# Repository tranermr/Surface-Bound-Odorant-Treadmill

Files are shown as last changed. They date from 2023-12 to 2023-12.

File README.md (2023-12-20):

# Surface-Bound-Odorant-Treadmill

One of the important subsets of odors sources used in olfactory navigation is surface-bound sources, which can broadly take the form of point sources or trails. Here, we present an automated treadmill design capable of dynamically printing odor trails of arbitrary lengths and configurations, and with closed-loop control of speed based on the animal’s movement. This design is presented and the utility demonstrated in a corresponding paper studying surface-bound odor trail interactions in locusts (in submission).The uploaded design incorporates some improvements not reflected in the version used in the published paper (i.e. the modification of some components to reduce paper jams, and quality of life improvements). The design is provided in four directories, containing the mechanical components, the electrical component design, and the software and firmware for operation.

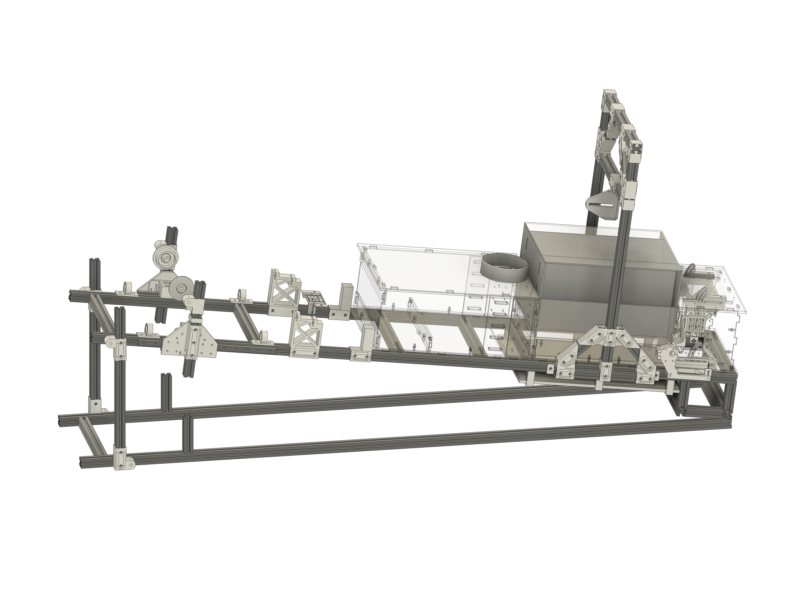
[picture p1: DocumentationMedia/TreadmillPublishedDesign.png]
Photo of assembled treadmill


The treadmill is designed to enable long-duration interactions with surface-bound odor trails of arbitrary length. Below you can see a video of a locust engaged in a bout of trail following with an odor trail, where the treadmill advances once the locust approaches the front of the behavior chamber, revealing more trail for the locust to interact wtih.

Video of locust following an odor trail

The treadmill is comprised of a series of modules sequentially connected and mounted on an 80-20 frame enabling different slopes to be configured. The design of the mechanical components is provided as an .f3d file, openable using Fusion 360, which is available in [educational](https://www.autodesk.com/campaigns/education/fusion-360-education), or [professional or free versions](https://www.autodesk.com/products/fusion-360/personal/compare).

In the mechanical design file, the design is organized by modules, with the exception of the 'behavior chamber' and 'driver' modules, which are merged in the present design. The organizational structure is arranged to reflect all modules independently for any future revisions. Further details regarding each of the design categories is provided below.

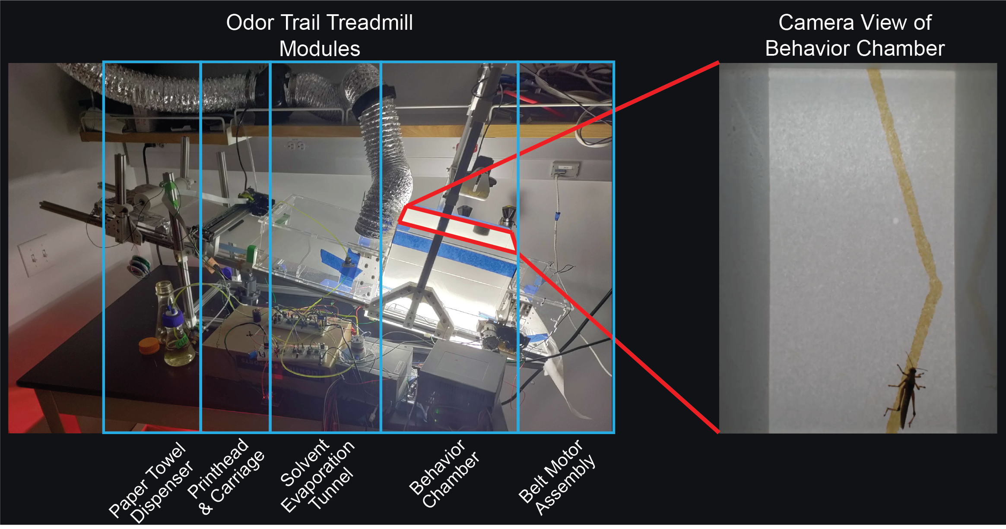
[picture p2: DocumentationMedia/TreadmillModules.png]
Treadmill modules, and top view of behavior chamber


## Mechanical Components
The components of each treadmill module are broken out below. Each module section contains a list of the parts not 3D printed or laser cut from acrylic, as well as suggestions to ease assembly.

### Frame
The treadmill frame is made of 20mm extruded aluminum (2020). The recommended parts list for the frame is

<ins>Misumi</ins>
| Description				| Part Number 		| Quantity|
| ------------- 			|:-------------:	| -----:|
| Aluminum Extrusions 			| HFS5-2020-1500 	| 6 	|
| Aluminum 20mm Brace - optional	| HBLFSNF5-C-SEC 	|   8 	|
| Square Nuts (100 Pack)		| HNKK5-5      		|   2 	|
| Hinges 				| HHPSN5-SET      	|   2 	|

<ins>Grainger</ins>
| Description			| Part Number 		| Quantity|
| ------------- 		|:-------------:	| -----:|
| Bolts M5-0.8 10mm (50 Pack)	| 53GJ15	 	| 5 	|

<ins>Amazon</ins>
| Description			| Part Number 		| Quantity|
| ------------- 		|:-------------:	| -----:|
| Aluminum 20mm Brace (20 Pack)	| [20mm m5 compatible](https://a.co/d/7hRMjW2)	| 3 	|

If cutting yourself, a chopsaw and an aluminum cutting blade (e.g. [Tomax aluminum blade](https://a.co/d/3ZllS9o)) will will greatly ease making accurate and fast cuts compared to a hacksaw.

The HBLFSNF5 braces are optional because while they were used to mount the acrylic components of the evaporation tunnel to the aluminum frame, it is just as practical to mount to the alumium extrusion directly. They are included as an option, but are not suggested.

### Paper Towel Dispenser
The paper towel dispenser is constructed of two vertical mounting bars. The paper towel is hung between the bars on a 1/4" threaded rod, with tension applied to the side of the mount using a compressed spring adjustable via a pair of wingnuts. The position of the two bars (and thereby the alignment of the paper towel with the rig) can be adjusted by advancing or retracting one side or the other using the adjustment screws on the sides. 

<ins>Amazon</ins>
| Description			| Part Number 		| Quantity|
| ------------- 		|:-------------:	| -----:|
| MGN12H 300mm linear rail guide| [MGN12H Rail](https://a.co/d/gDsAsOn)	| 2 	|
| MGN12H Carriage Block		| [MGN12H Carriage Block(https://a.co/d/gDsAsOn)	| 4 	|
| Spring Set			| [SP 9702](https://a.co/d/3PLaYax)	| 1 	|
| Bearing set			| [6202-2RS](https://a.co/d/721F6t8)	| 4 	|

<ins>Hardware Store (or Amazon, etc.)</ins>
| Description			| Part Number 		| Quantity|
| ------------- 		|:-------------:	| -----:|
| 1/4" Threaded Rod 1 foot long	| na			| 3 	|
| 1/4" Nuts			| na			| 20 	|
| 1/4" Wingnuts			| na			| 3 	|

<ins>Grainger</ins>
| Description			| Part Number 		| Quantity|
| ------------- 		|:-------------:	| -----:|
| 1/4" Fender Washers		| 35YU76		| 2 	|

<ins>Assembly of left, right alignment adjustments.</ins>
In the following assembly guides 3D printed components are placed in quotes and referred to by their body names in the Fusion 360 file.

The alignment assemblies consist of a 1' threaded rod, with the following parts threaded on in sequence, pictured below: 
 - Assembly 1: hex nut - "AlignmentScrewInner" - 6202 bearing - "AlignmentScrewInner" - hex nut 
 - Assembly 2: hex nut - spring - hex nut 
 - Assembly 3: hex nut - "AlignmentScrewInner" - 6202 bearing - "AlignmentScrewInner" - hex nut 
 - Assembly 4: hex nut - wing nut

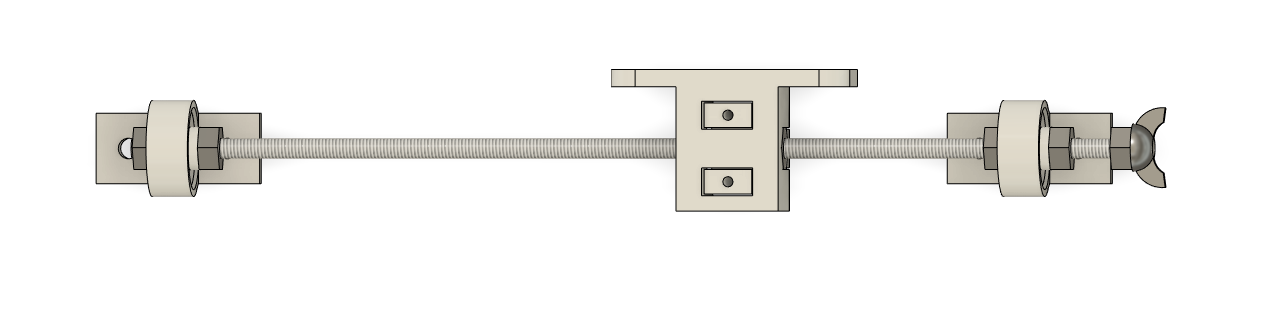
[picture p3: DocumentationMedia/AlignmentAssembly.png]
Left/right alignment assemblies


Assemblies 1 and 3 hold the threaded rod and allow rotation.
Assembly 2 is clamped by the "AlignmentBoltClamp" that moves the vertical mounting bar forward or backwards as the threaded rod is rotated. The spring compressed between the two bolts serves to prevent backlash and reduce wobble in the assembly; this is pictured below.
Assembly 4 provides an easy way to rotate the threaded rod, by locking the wing nut in place using the hex nut.

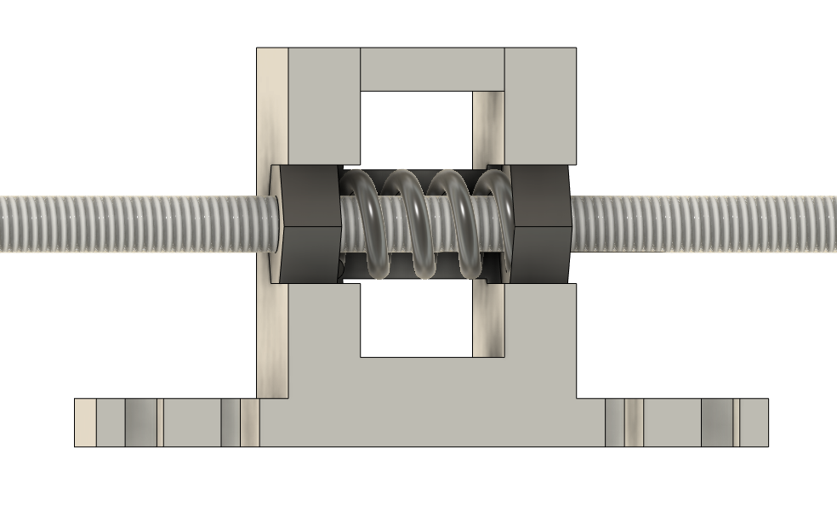
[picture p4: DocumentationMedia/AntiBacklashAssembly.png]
Vertical bar linkage - Assembly 2


<ins>Assembly of paper towel suspension rod.</ins>
The alignment assemblies consist of a 1' threaded rod, with the following parts threaded on in sequence, pictured below: 
 - Assembly 1: wing nut - "PaperTowelHolderBrace" - hex nut 
 - Assembly 2: hex nut - "PaperTowelInsertInner" - hex nut 
 - Assembly 3: hex nut - hex nut - "PaperTowelInsertInner" - fender washer - spring - fender washer - hex nut - hex nut
 - Assembly 4: hex nut - "PaperTowelHolderBrace" - hex nut 

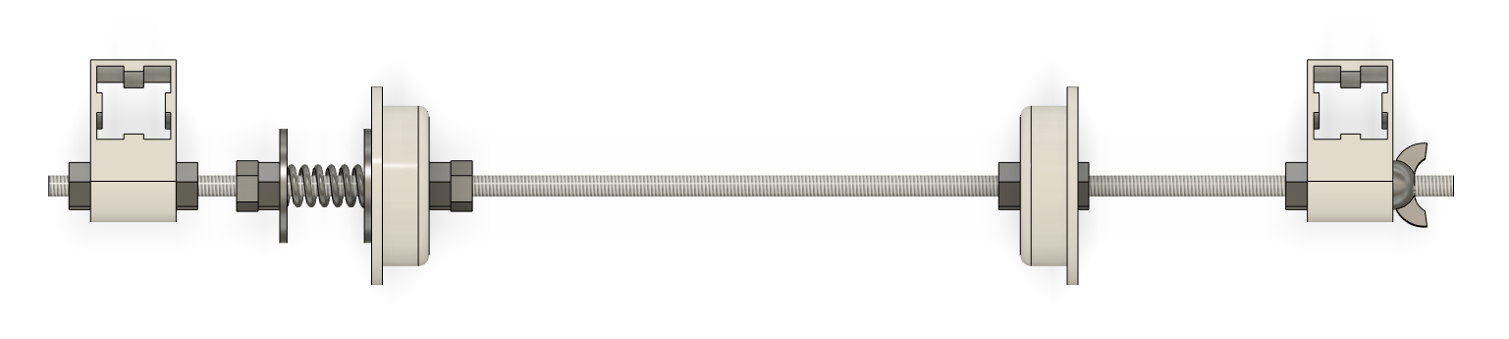
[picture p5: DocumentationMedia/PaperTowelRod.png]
Paper towel suspension rod


Assembly 1 holds the threaded rod, but allows the brace to be removed for changing the paper towel roll.
Assembly 2 holds the inner insert for the bearing on which the paper towel pivots.
Assembly 3 holds the inner insert for the second bearing on which the paper towel pivots. In addition, the fender washer compressed against the "TowelInsertOuter" provides friction which tensions the paper towel. By adjusting compression on the spring (or switching to a different spring) the paper towel tension can be tuned to keep the paper towel taut, but minimally burden the driver motor.
Assembly 4 holds the threaded rod.

### Print Carriage Assembly
The print assembly is centered around the print carriage assembly removed from an HP Photosmart C6180 inkjet printer. The inkjet printing assembly is removed, and the "PrintCarriageInsert" is inserted in its place. 

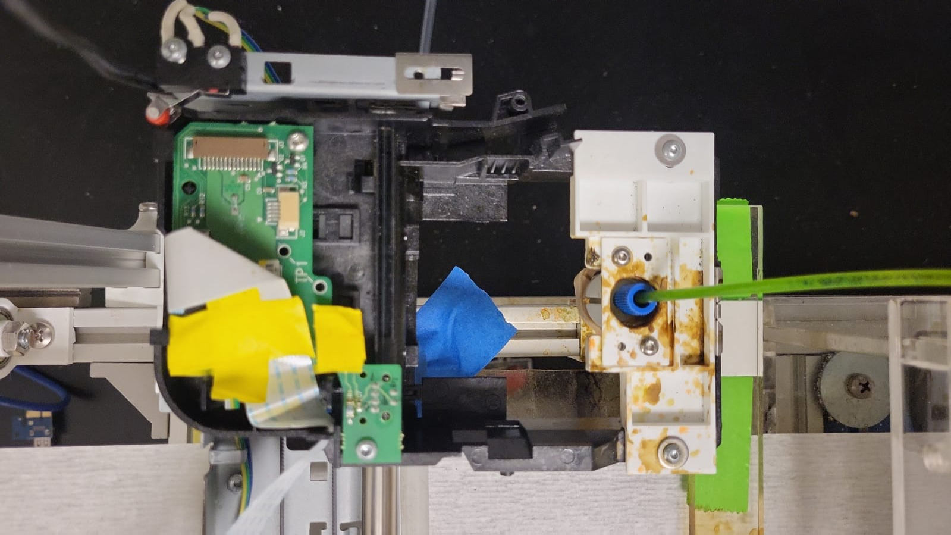
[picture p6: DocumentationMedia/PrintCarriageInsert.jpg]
Print carriage insert


The linear encoder from the print carriage PCB is accessed by connecting to the quadrature encoder using the ribbon cable. This was achieved by producing a breakout board on a piece of FR-4 Copper Clad board, soldering on a compatible ribbon cable mount, and soldering on male 2.54 header pins (pictured below). However, soldering wires directly instead of the pins would reduce risk of accidental disconnection. The traces on the print carriage PCB can also be soldered to directly to avoid needing to construct an adapter. 

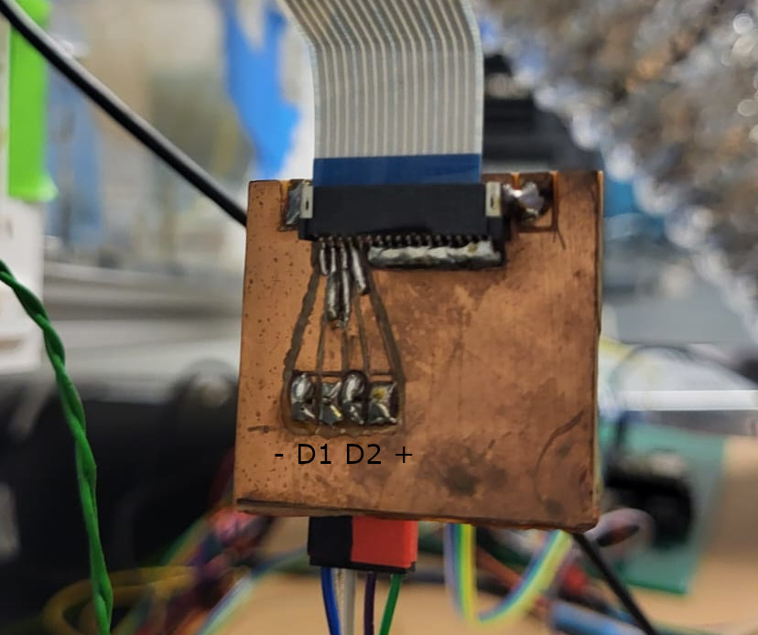
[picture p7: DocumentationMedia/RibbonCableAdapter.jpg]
Print carriage adapter board


<ins>Amazon</ins>
| Description			| Part Number 								| Quantity|
| ------------- 		|:-------------:							| -----:|
| Copper-Clad Board		| [FR-4](https://a.co/d/aHfhtKA)					| 1 	|

<ins>Digikey</ins>
| Description		| Part Number 				| Quantity|
| ------------- 	|:-------------:			| -----:|
| Ribbon Cable Mount	| 18 Pin Flex PCB Mount			| 1 	|

### Print System Assembly
The pressurized print system is comprised of four parts connected in sequence:
 - Air pressure regulator 
 - Print solution reservoir
 - Solenoid valve
 - Printhead

<ins>Printhead assembly</ins>
The printhead construction is the most challenging to fabricate. A 15mm segment is cut from the nylon rod, and drilled using a 6mm bit. One end is tapped to M6 to accomodate the brass printhead, and the other is drilled with a 1/4" bit and tapped to 1/4"-28 to accomodate the adapter for the 1/8" tubing. The printhead threads are wrapped with PTFE tape, and screwed into the nylon segment, taking care that excess PTFE tape is removed prior to insertion. 

Note: If a lathe is available it will greatly ease accurate drilling of the hole, and cutting of the segments. 

Note 2: If the holes are centered (e.g. drilled on a lathe), multiple printheads can be made to ease cleaning and clearing of any clogs that may occur.

<ins>Full assembly</ins>
The regulator is assembled by connecting 1/4" push connect fittings into the inlet and outlet ports. The inlet port is connected to a pressurized air system, and the outlet is connected to the 1/4" tubing. A length of 1/8" Kynar Flex tubing is coated with superglue, and rapidly inserted 5-10cm into the 1/4" tubing, and allowed to dry. The 1/8" tubing is then connected to the Odor Reservoir Cap, and secured in place using the 1/4"-28 adapter with the tubing protruding just inside the cap. A second length of tubing is inserted to the bottom of the flask and similarly secured. The other end of the second length of tubing is then inserted into the inlet port of the Clippard solenoid valve and secured. The outlet port of the solenoid is connected to a third length of tubing, sufficient to run from the position of the solenoid to the print carriage at all points of travel. This will depend on the location where the solenoid is mounted. The third length of tubing is then connected to the printhead using the same 1/4"-28 adapters, and the printhead is inserted into the print carriage to the depth where it just contacts the surface of the paper towel.

<ins>Clippard</ins>
| Description		| Part Number 																| Quantity|
| ------------- 	|:-------------:															| -----:|
| Solenoid valve	| [NR3-2-12, Imperial, Vac to 30psi, 2-way NC, In line ports, 1/4-28 UNF port, 12V](https://www.clippard.com/part/NR3-2-12)		| 1	|

<ins>Amazon</ins>
| Description			| Part Number 								| Quantity|
| ------------- 		|:-------------:							| -----:|
| Nylon Rod 			| [Nylon Rod, 1/2" diameter, 1' length](https://a.co/d/fmmiPHx)		| 1	|
| Brass Printhead Set (4)	| [0.1mm x M6 thread](https://a.co/d/aySFkyX)				| 1 	|

<ins>Cole Parmer</ins>
| Description					| Part Number 																| Quantity|
| ------------- 				|:-------------:															| -----:|
| Odor Reservoir Cap				| [EW-12018-03](https://www.coleparmer.com/i/cole-parmer-vaplock-solvent-delivery-cap-two-1-4-28-ports-gl45-1-ea/1201803)		| 1	|
| 1/8" Tubing to 1/4"-28 adapter (10 pack)	| [EW-12020-08](https://www.coleparmer.com/i/cole-parmer-vaplock-fitting-blue-pp-w-yellow-etfe-straight-compression-to-threaded-adapter-1-8-od-x-1-4-28-unf-m-10-pk/1202008)		| 1|

<ins>VWR</ins>
| Description					| Part Number 																| Quantity|
| ------------- 				|:-------------:															| -----:|
|Transfer Tubing, Kynar Flex™ 2750 PVDF, 1/16" ID x 1/8" OD; 50 ft |  [MFLX95100-01](https://us.vwr.com/store/product/39208964/masterflex-transfer-tubing-kynar-flextm-2750-pvdf-avantor) | 1 |

<ins>Grainger</ins>
| Description					| Part Number 																| Quantity|
| ------------- 				|:-------------:															| -----:|
|PVC Tubing 1/4"OD 1/8"ID |  [2LPT1](https://www.grainger.com/product/TYGON-Tubing-Tygon-S3-B-44-3-2LPT1) | 1 |
|PTFE Tape|  [3PDL5](https://www.grainger.com/product/ANTI-SEIZE-TECHNOLOGY-ANTI-SEIZE-TECH-Thread-Sealant-3PDL5) | 1 |

### Evaporation Tunnel
The plexiglass panels of the evaporation tunnel should be cut, the 3D printed components printed, and all assembled according to the .f3d file. The top tube mount should be connected to the exhaust tubing, and routed to an exhaust line. If additional flow is needed the exhaust fan can be used to increase the exhaust flow.

<ins>Amazon</ins>
| Description			| Part Number 					| Quantity|
| ------------- 		|:-------------:				| -----:|
| Exhaust Fan (optional)	| [MGN12H Rail](https://a.co/d/gDsAsOn)		| 1 	|
| Exhaust Tubing 		| [MGN12H Rail](https://a.co/d/gDsAsOn)		| 1 	|

<ins>Hardware Store (or Amazon, etc.)</ins>
| Description			| Part Number 		| Quantity	|
| ------------- 		|:-------------:	| -----:	|
| 1/4" Acrylic Sheet Clear 	| na			| na 		|

### Behavior Chamber
The plexiglass panels should be cut, the 3D printed components printed, and all assembled according to the .f3d file. The top and bottom panels of the behavior chamber are made of glass sheets; the side of the bottom sheet (and optionally the top sheet) should be trimmed to fit the width of the chamber (249mm) (see .f3d file). The top cover panel can be attached to the front of the behavior chamber using two strips of tape, positioned on the edges past the side of the behavior chamber. 

The inner sides of the behavior chamber acrylic sheets can be coated in fluon; this is most easily done by removing them from the behavior chamber, laying them flat on a counter, and applying the fluon using the brush dispenser in the parts list below. Before reapplying, the sides should be thoroughly cleaned using hot soap and water, and allowed to dry.

<ins>Hardware Store (or Amazon, etc.)</ins>
| Description			| Part Number 		| Quantity	|
| ------------- 		|:-------------:	| -----:	|
| 3/32" Glass Sheet (10" x 12")	| [Shape Glass](https://www.homedepot.com/p/10-in-x-12-in-x-0-09375-in-Clear-Glass-91012/300068325)			| 2 		|
| 1/8" Acrylic Sheet White	| na			| na 		|
| 1/4" Acrylic Sheet Clear	| na			| na 		|

<ins>Amazon</ins>
| Description			| Part Number 		| Quantity	|
| ------------- 		|:-------------:	| -----:	|
| Fluon				| [byFormica Fluon Plus](https://a.co/d/d54PUUA) | 1 		|

### Driver
The plexiglass panels should be cut, the 3D printed components printed, and all assembled according to the .f3d file. The driver and guide rod assemblies, as well as the nylon bushings, were removed from the same HP Photosmart C6180 inkjet printer that supplied the print carriage. One repair was made by replacing the motor with a larger 12V motor removed from [this](https://a.co/d/cd3eFye) peristaltic pump assembly. However, a motor such as [this](https://a.co/d/8RF5Nmk) should also be compatible with the mounting bracket, and the wide range of speeds would enable a fine tuning of maximum speed against torque for the driver assembly.

### Camera Assembly
The aluminum extrusion sections should be cut, the 3D printed components printed, and all assembled according to the .f3d file. The logitech webcam base can be mounted using the 1/4" threaded rod and nut, enabling easy positioning above the behavior chamber.

<ins>Amazon</ins>
| Description			| Part Number 					| Quantity|
| ------------- 		|:-------------:				| -----:|
| Logitech C920S		| [C920S](https://a.co/d/djdxm9s)		| 1 	|

<ins>Hardware Store (or Amazon, etc.)</ins>
| Description			| Part Number 		| Quantity|
| ------------- 		|:-------------:	| -----:|
| 1/4" Threaded Rod 1 inch long	| na			| 1 	|
| 1/4" Nuts			| na			| 1	|

### Backlight
The backlight is comprised of a 1/4" thick plexiglass base upon which IR and white LED strips are alternately layed. The LED strips are soldered together such that either the white (visible) or IR (non-visible) backlight can be used. The light diffuser panels should be cut according to the .f3d file, and can be inserted at multiple levels in the diffuser mount, up to a maximum of 6 panels. 1-2 sheets of paper should be layed over the top of diffuser panels to better distribute the illumination.

<ins>Hardware Store (or Amazon, etc.)</ins>
| Description				| Part Number 						| Quantity|
| ------------- 			|:-------------:					| -----:|
| 1/4" Acrylic Sheet Clear		| na							| 1 	|
| IR LED Strip				| [SMD3528 850nm LED Strip](https://a.co/d/do7MLOz)	| 1	|
| White LED Strip			| [SMD5050 White LED Strip](https://a.co/d/cHSYJyx)	| 1	|
| Light Diffuser Sheet			| [Diffuser](https://www.homedepot.com/p/OPTIX-23-75-in-x-47-75-in-Clear-Plastic-Acrylic-Prismatic-Ceiling-Light-Panel-1A20083A/100550880)	| na	|
| White Printer Paper (8.5"x14")	| [Paper](https://a.co/d/dwqtg2p)			| 1	|

<ins>Grainger</ins>
| Description			| Part Number 		| Quantity	|
| ------------- 		|:-------------:	| -----:	|
| Bolts M5-0.8 35mm (50 Pack) 	| 53GJ20		| 1 		|

## Electrical Components
The circuit layout and PCB design are provided in the form of a KiCAD project. A parts list is provided below:

<ins>Parts List</ins>
| Description		| Part Number 			| Quantity|
| ------------- 	|:-------------:		| -----:|
| Teensy 3.5			| Teensy 3.5		| 1 	|
| 5V Regulator			| L7805CV Through Hole	| 2 	|
| Optoisolator			| 6N137 Through Hole	| 10 	|
| Hex Inverter			| SN74HC14N Through Hole| 2 	|
| TIP41C Transistor		| Tip41C Through Hole	| 2 	|
| Diode				| 1N4002 Through Hole	| 2 	|
| Filter Capacitor		| 4.7uF Through Hole	| 11 	|
| Limit Switch Bias Resistor 1	| 100 Ohm SMD	 	| 1 	|
| Limit Switch Bias Resistor 2	| 1.2 KOhm SMD	 	| 1 	|
| Optoisolator Filter Cap	| 1uF SMD		| 10 	|
| Optoisolator LED Resistor	| 360 Ohm SMD		| 10 	|
| Optoisolator Bias Resistor	| 1 KOhm SMD		| 10 	|

Note: Only two of the four capacitor slots around the voltage regulator are populated. The extra slots can be used if additional filtering is required.

## Software Components
The software is provided in the form of a python script and an embedded program for the Teensy 3.5. 

### Embedded Firmware
The embedded firmware can be uploaded using the [Arduino IDE](https://www.arduino.cc/en/software). 

### Python Software Script
The python software script contains several values that must be configured on the experimental computer in order for communication with the microcontroller (and thereby control over the treadmill) to be achieved. Namely, the serial port and camera input must be specified correctly. To do this 

cap = cv2.VideoCapture(0) in camMain can be set to different camera inputs by changing the '0' to a different number corresponding to the desired input.

ser = serial.Serial('COM4', 2000000, writeTimeout=0) in serMain can be configured to read from a different com port, e.g. 'COM3', and should be configured to match the serial port on which the treadmill is connected.

In addition, the threshold for binarizing the image in order to track the locust must be configured by adjusting the threshold value in the calcSpeed function. Note that this will change when switching between visible and IR backlighting. This can be done by modifying the value of '20' in the below code line to a value found to effectively isolate the animal on the treadmill with the given backlight. 

bw = cv2.threshold(gray, 20, 255, cv2.THRESH_BINARY_INV)[1]

If switching between visible and IR conditions, two versions of the above line can be written, and the unused one commented out prior to running the treadmill.

# Considerations for building
If you are considering building this treadmill there are several considerations that you may want to take into account. The first is whether greater flexibility of odorants, or the width and precision of the trail are more important for your purposes. If some odorants that are incompatible with an inkjet cartridge will be used, then the pressurized reservoir system described in the Print System Assembly section will be the most suitable. However, if the odor panel is limited to odorants that would be compatible with a print cardtridge, then repurposing a print cartridge may provide more consistent and smaller trails. Such a method was used by Dr. Venkatesh Murthy to produce odor trails for mice (see odor trails sections in the [DeepLabCut paper](https://www.nature.com/articles/s41593-018-0209-y#Ack1) by Mathis et al.).

Another consideration is whether to use the optical encoder system used here for the treadmill and print carriage positions. While highly precise, stepper motors likely would produce sufficiently accurate positioning, and may be easier to obtain and configure. This is especially useful if considering expanding the treadmill by adding a second printhead or a system for depositing rewards on the trail (see Suggested Directions for Future Modifications and Expansions) given that the Teensy 3.5 only has two hardware quadrature decoders, both of which are already allocated to the belt encoder and print carriage encoders. Furthermore, if hardware quadrature decoding is not required it would also be possible to utilize the faster Teensy 4.x series microcontrollers or other alternatives.

# Suggested Directions for Future Modifications and Expansions
- Second printhead
- Use of an inkjet module for higher precision trails (albeit with a more constrained odor panel)
- Use of stepper motors instead of the PID controlled print carriage assembly.
- Reward depositor or printer (behavior chamber front slot will need to be raised to avoid rewards being scraped off the paper towel before entering the behavior chamber)

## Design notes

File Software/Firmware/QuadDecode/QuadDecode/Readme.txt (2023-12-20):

Code supplied by tlb on the PJRC forums
https://forum.pjrc.com/index.php?threads/hardware-quadrature-code-for-teensy-3-x.26803/

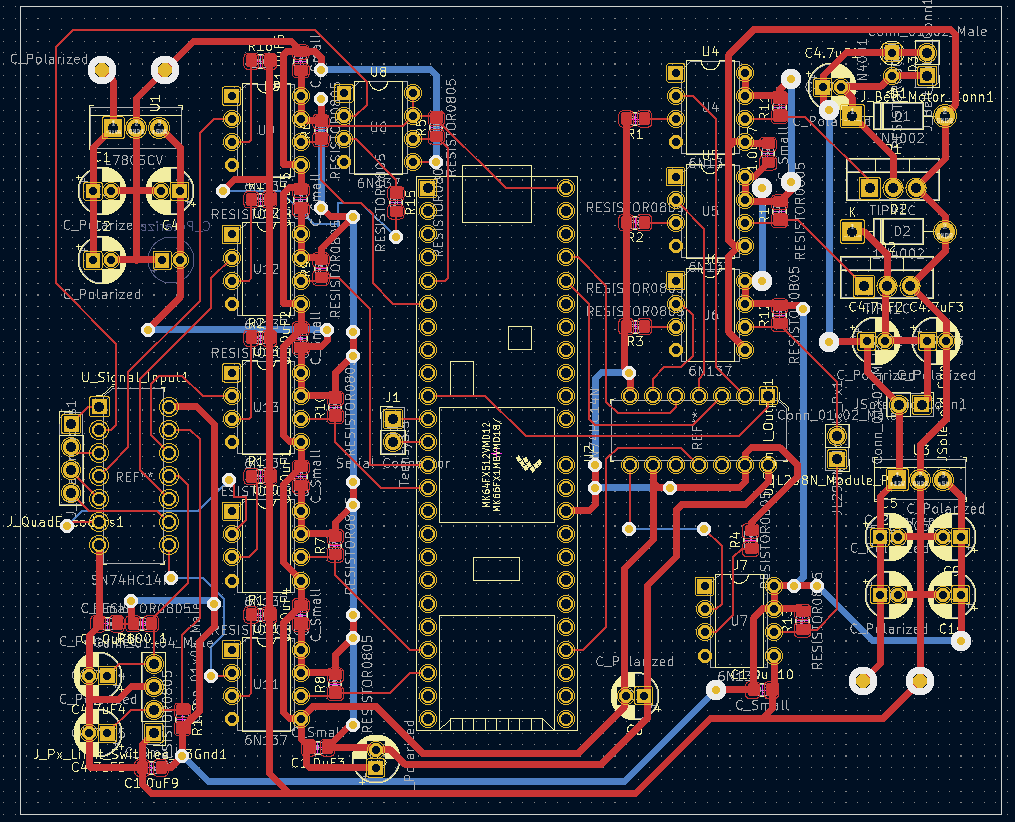
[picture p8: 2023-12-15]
Electrical/PCB_Black.PNG

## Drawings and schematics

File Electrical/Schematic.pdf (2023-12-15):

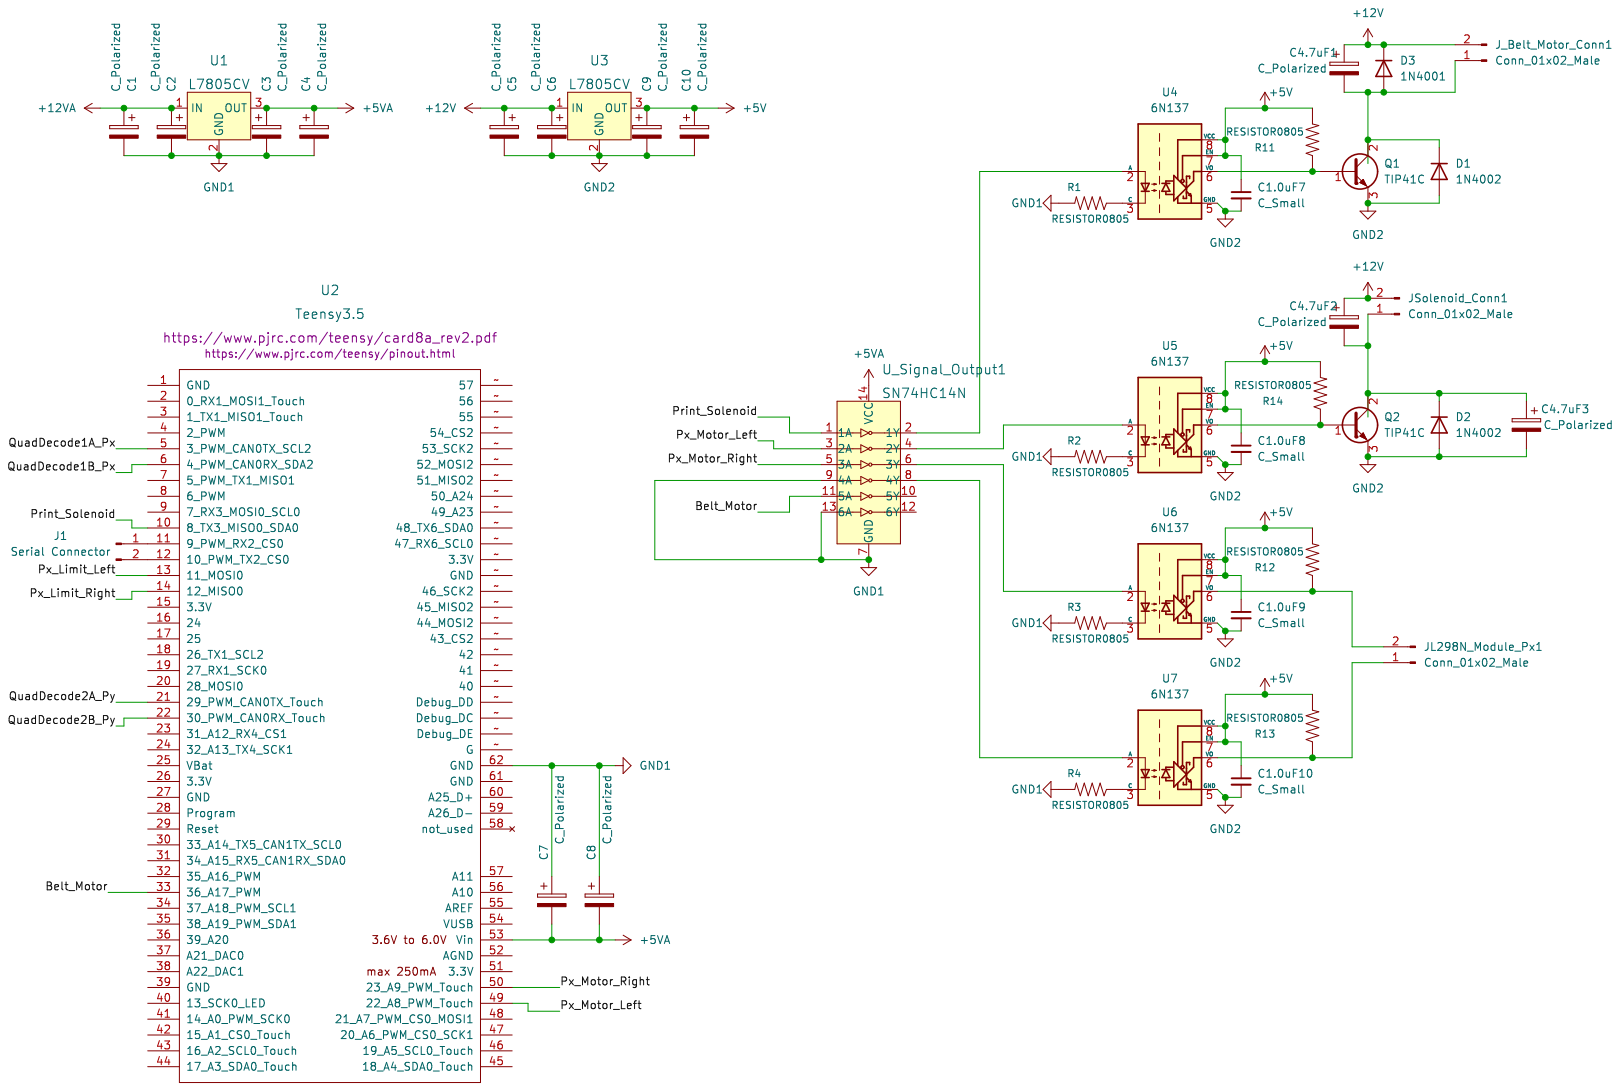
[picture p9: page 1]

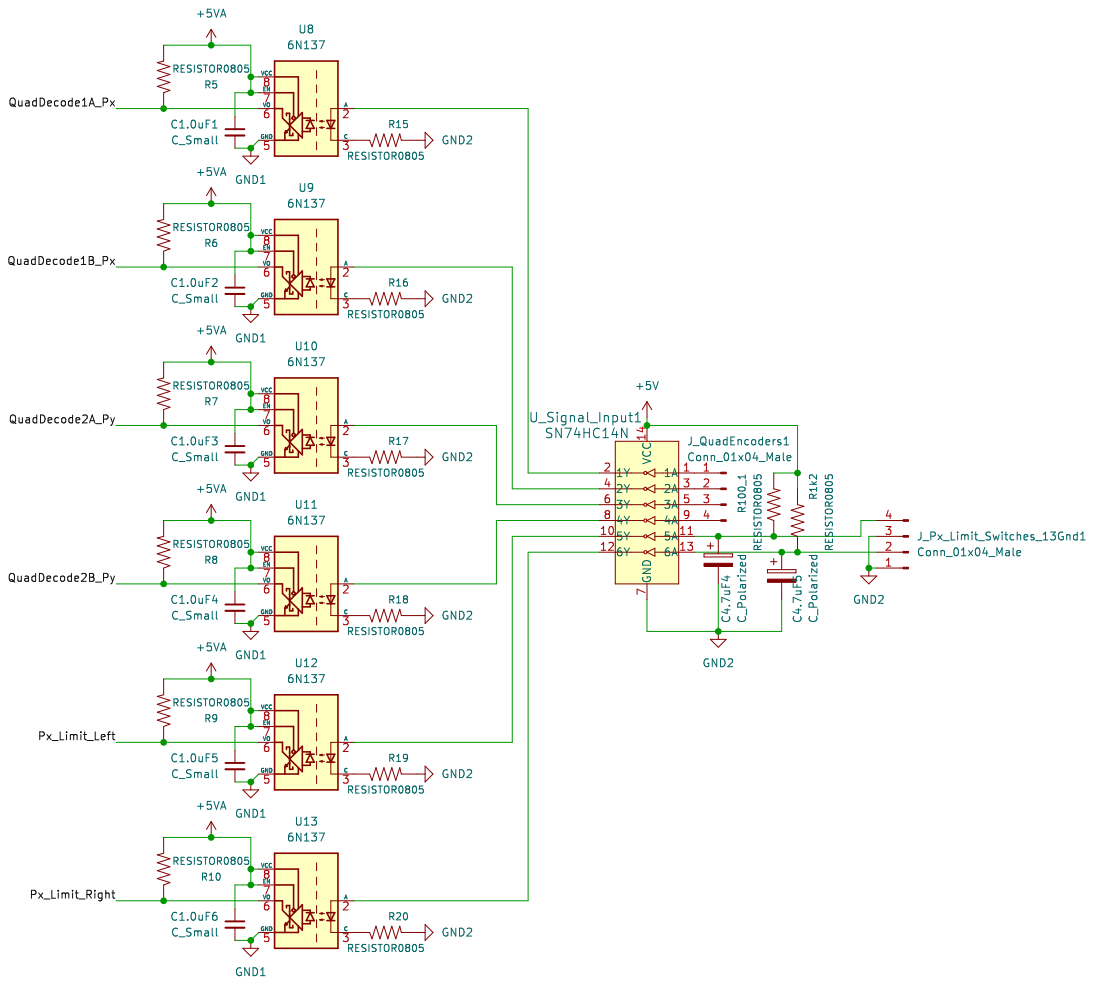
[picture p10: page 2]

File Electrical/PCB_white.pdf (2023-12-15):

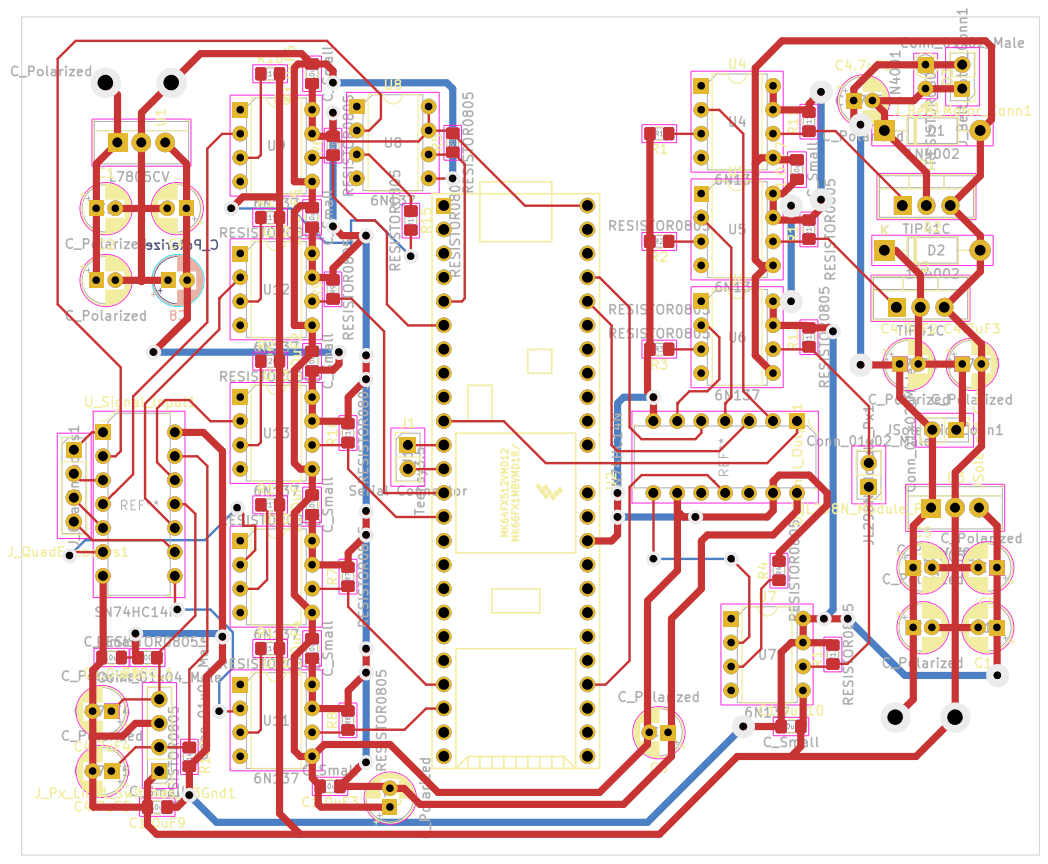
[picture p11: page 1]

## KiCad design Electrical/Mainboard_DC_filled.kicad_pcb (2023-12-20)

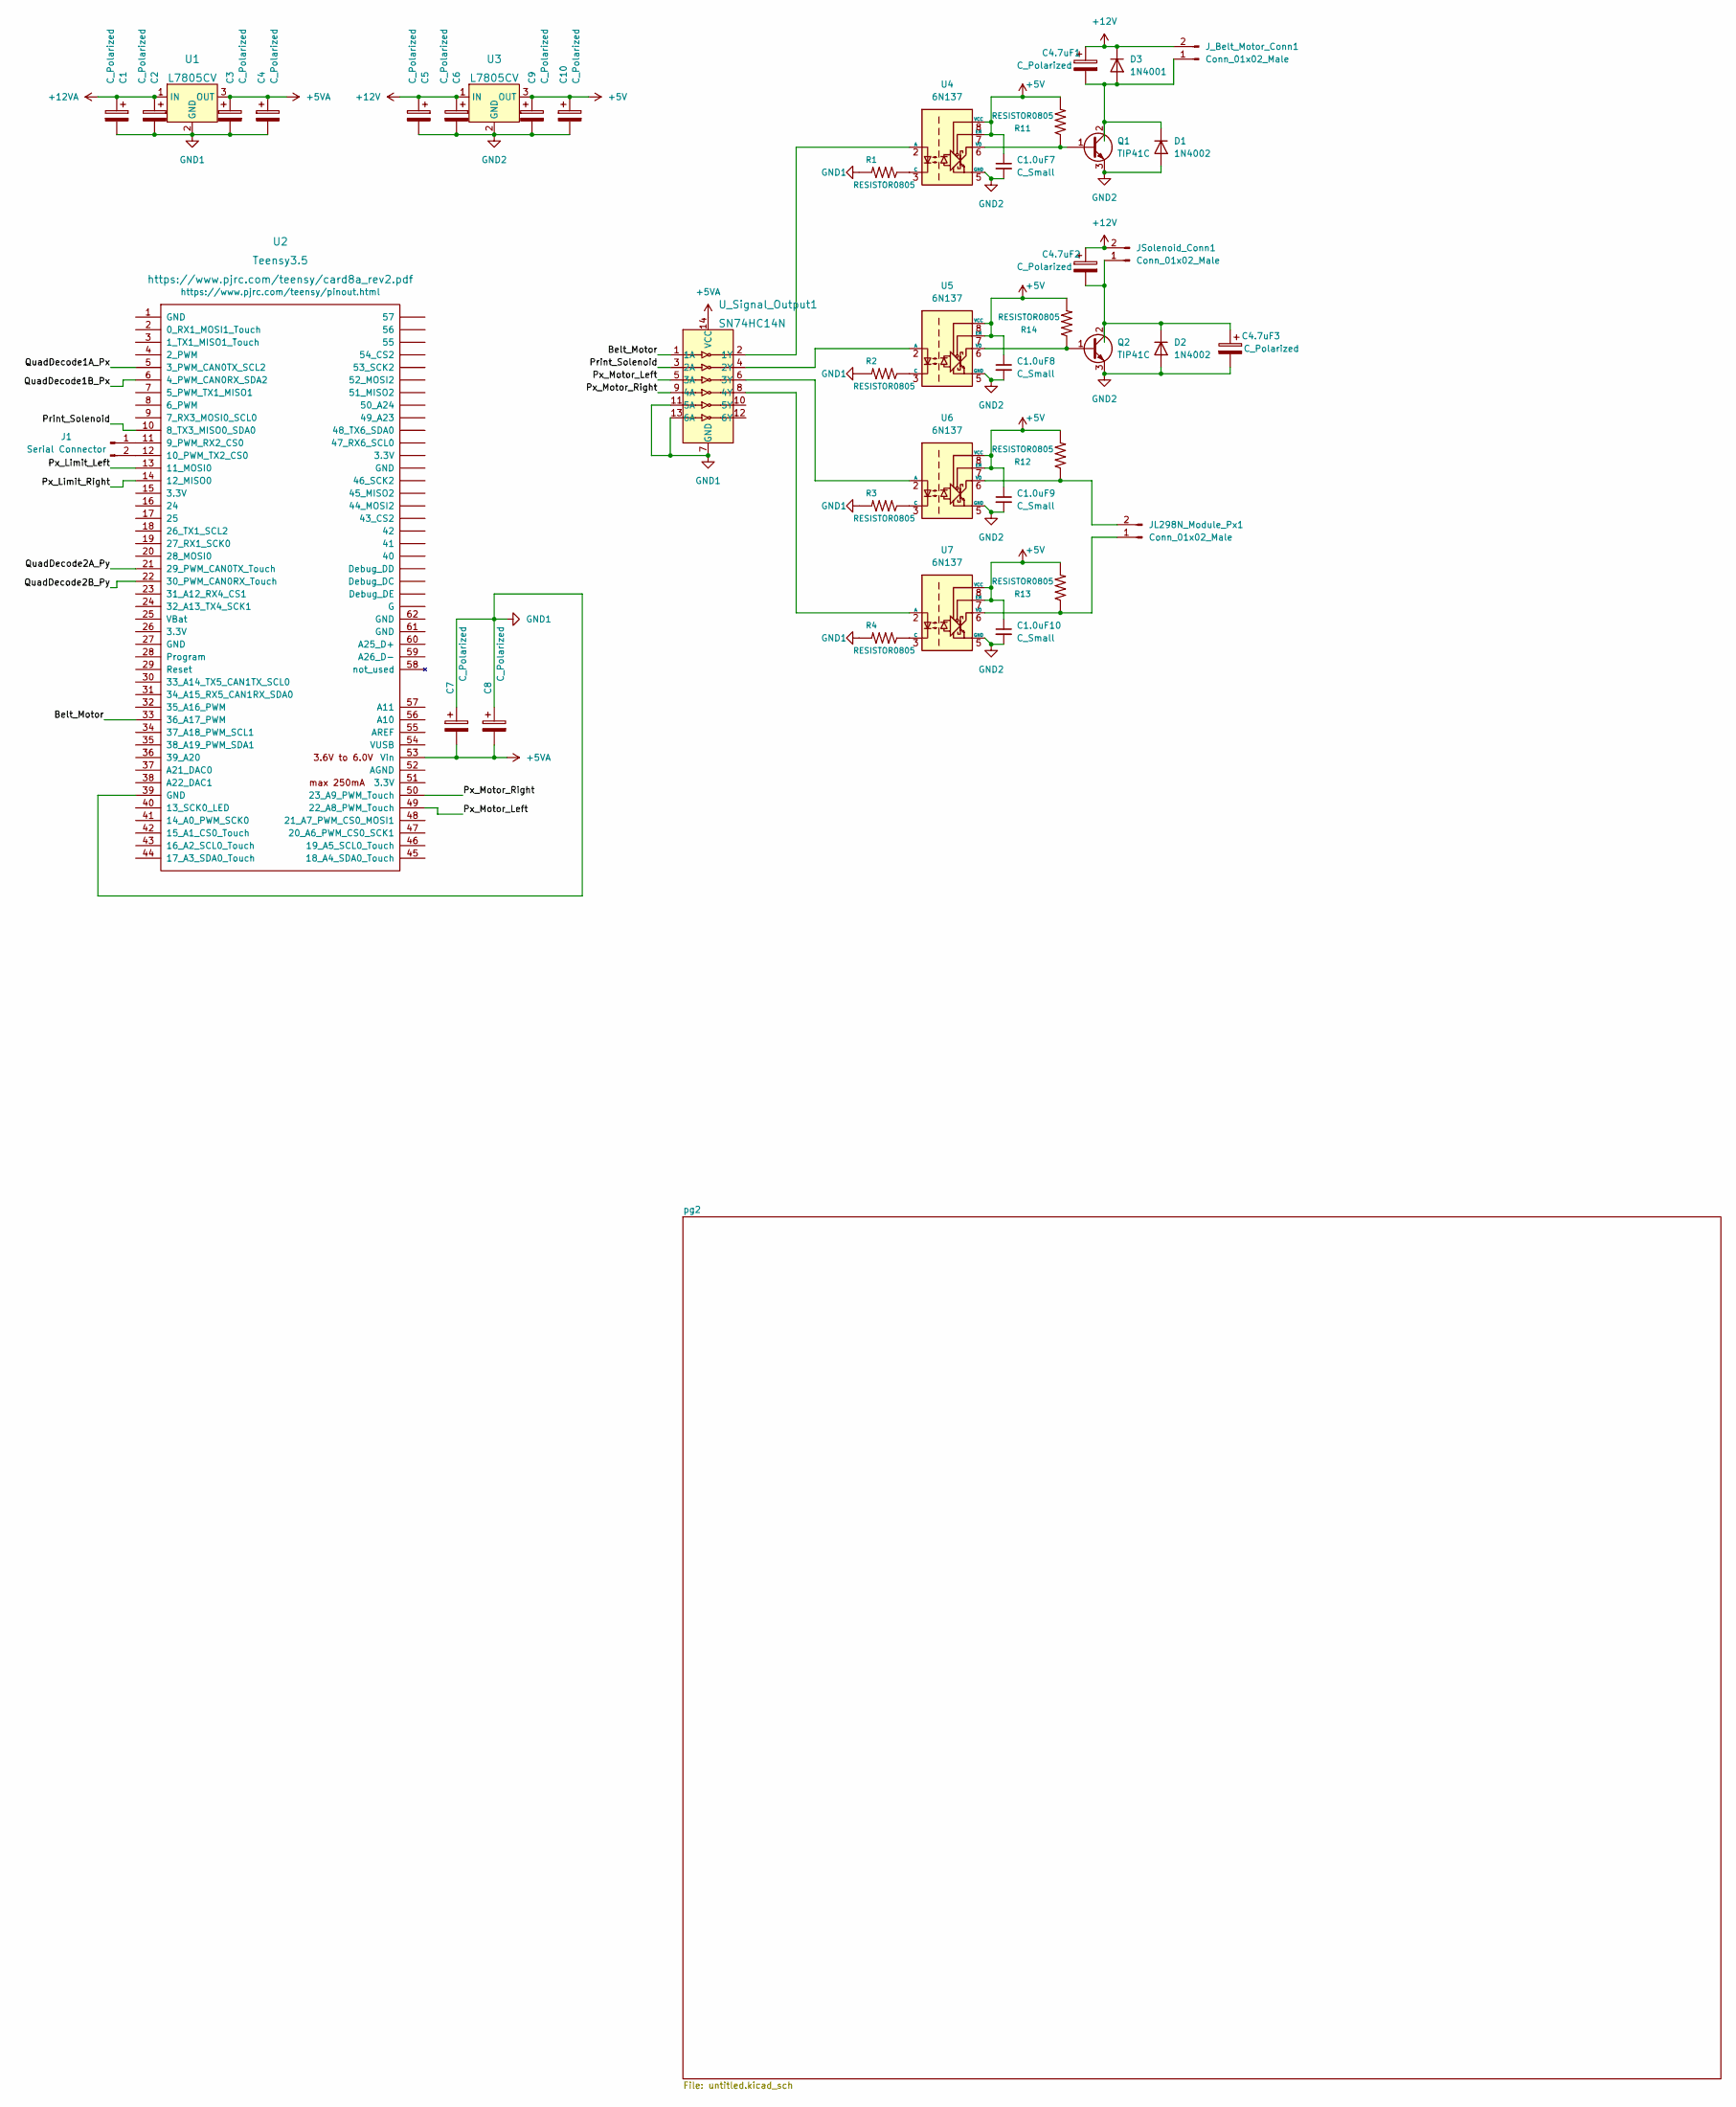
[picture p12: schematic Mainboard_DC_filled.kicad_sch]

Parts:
C1, C2, C3, C4, C4.7uF1, C4.7uF2, C4.7uF3, C5, C6, C7, C8, C9, C10: C_Polarized; CP_Radial_D5.0mm_P2.00mm
C1.0uF7, C1.0uF8, C1.0uF9, C1.0uF10: C_Small; C_0805_2012Metric_Pad1.18x1.45mm_HandSolder
D1, D2: 1N4002; D_DO-41_SOD81_P10.16mm_Horizontal
D3: 1N4001; D_DO-41_SOD81_P10.16mm_Horizontal
J1: Serial Connector; PinHeader_1x02_P2.54mm_Vertical
JL298N_Module_Px1: Conn_01x02_Male; PinHeader_1x02_P2.54mm_Vertical
JSolenoid_Conn1: Conn_01x02_Male; PinHeader_1x02_P2.54mm_Vertical
J_Belt_Motor_Conn1: Conn_01x02_Male; PinHeader_1x02_P2.54mm_Vertical
Q1, Q2: TIP41C; TO-220-3_Vertical
R1, R2, R3, R4, R11, R12, R13, R14: RESISTOR0805; R_0805_2012Metric_Pad1.20x1.40mm_HandSolder
U1, U3: L7805CV; TO-220-3; MPN L7805CV; Digi-Key_PN 497-1443-5-ND
U2: Teensy3.5; Teensy35_36
U4, U5, U6, U7: 6N137; DIP-8_W7.62mm
U_Signal_Output1: SN74HC14N; DIP-14_W3mm; MPN SN74HC14N; Digi-Key_PN 296-1577-5-ND

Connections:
+5V: C1.0uF7.1, C1.0uF8.1, C1.0uF9.1, C1.0uF10.1, C9.1, C10.1, R11.2, R12.2, R13.2, R14.2, U3.3 (OUT), U4.7 (EN), U4.8 (VCC), U5.7 (EN), U5.8 (VCC), U6.7 (EN), U6.8 (VCC), U7.7 (EN), U7.8 (VCC); also elsewhere on the board
+5VA: C3.1, C4.1, C7.2, C8.2, U1.3 (OUT), U2.53 (Vin), U_Signal_Output1.14 (VCC); also elsewhere on the board
+12V: C4.7uF1.1, C4.7uF2.1, C5.1, C6.1, D3.1 (K), JSolenoid_Conn1.2, J_Belt_Motor_Conn1.2, U3.1 (IN)
+12VA: C1.1, C2.1, U1.1 (IN)
/Belt_Motor: U2.33 (36_A17_PWM), U_Signal_Output1.1 (1A)
/Print_Solenoid: U2.10 (8_TX3_MISO0_SDA0), U_Signal_Output1.3 (2A)
/Px_Limit_Left: U2.13 (11_MOSI0); also elsewhere on the board
/Px_Limit_Right: U2.14 (12_MISO0); also elsewhere on the board
/Px_Motor_Left: U2.49 (22_A8_PWM_Touch), U_Signal_Output1.5 (3A)
/Px_Motor_Right: U2.50 (23_A9_PWM_Touch), U_Signal_Output1.9 (4A)
/QuadDecode1B_Px: U2.6 (4_PWM_CAN0RX_SDA2); also elsewhere on the board
/QuadDecode2A_Py: U2.21 (29_PWM_CAN0TX_Touch); also elsewhere on the board
/QuadDecode2B_Py: U2.22 (30_PWM_CAN0RX_Touch); also elsewhere on the board
GND1: C1.2, C2.2, C3.2, C4.2, C7.1, C8.1, R1.2, R2.2, R3.2, R4.2, U1.2 (GND), U2.39 (GND), U_Signal_Output1.7 (GND), U_Signal_Output1.11 (5A), U_Signal_Output1.13 (6A); also elsewhere on the board
GND2: C1.0uF7.2, C1.0uF8.2, C1.0uF9.2, C1.0uF10.2, C4.7uF3.2, C5.2, C6.2, C9.2, C10.2, D1.2 (A), D2.2 (A), Q1.3 (E), Q2.3 (E), U3.2 (GND), U4.5 (GND), U5.5 (GND), U6.5 (GND), U7.5 (GND); also elsewhere on the board
unnamed: C4.7uF1.2, D1.1 (K), D3.2 (A), J_Belt_Motor_Conn1.1, Q1.2 (C)
unnamed: C4.7uF2.2, C4.7uF3.1, D2.1 (K), JSolenoid_Conn1.1, Q2.2 (C)
unnamed: J1.1, U2.11 (9_PWM_RX2_CS0)
unnamed: J1.2, U2.12 (10_PWM_TX2_CS0)
unnamed: JL298N_Module_Px1.1, R13.1, U7.6 (VO)
unnamed: JL298N_Module_Px1.2, R12.1, U6.6 (VO)
unnamed: Q1.1 (B), R11.1, U4.6 (VO)
unnamed: Q2.1 (B), R14.1, U5.6 (VO)
unnamed: U4.2 (A), U_Signal_Output1.2 (1Y)
unnamed: R1.1, U4.3 (C)
unnamed: U5.2 (A), U_Signal_Output1.4 (2Y)
unnamed: R2.1, U5.3 (C)
unnamed: U6.2 (A), U_Signal_Output1.6 (3Y)
unnamed: R3.1, U6.3 (C)
unnamed: U7.2 (A), U_Signal_Output1.8 (4Y)
unnamed: R4.1, U7.3 (C)

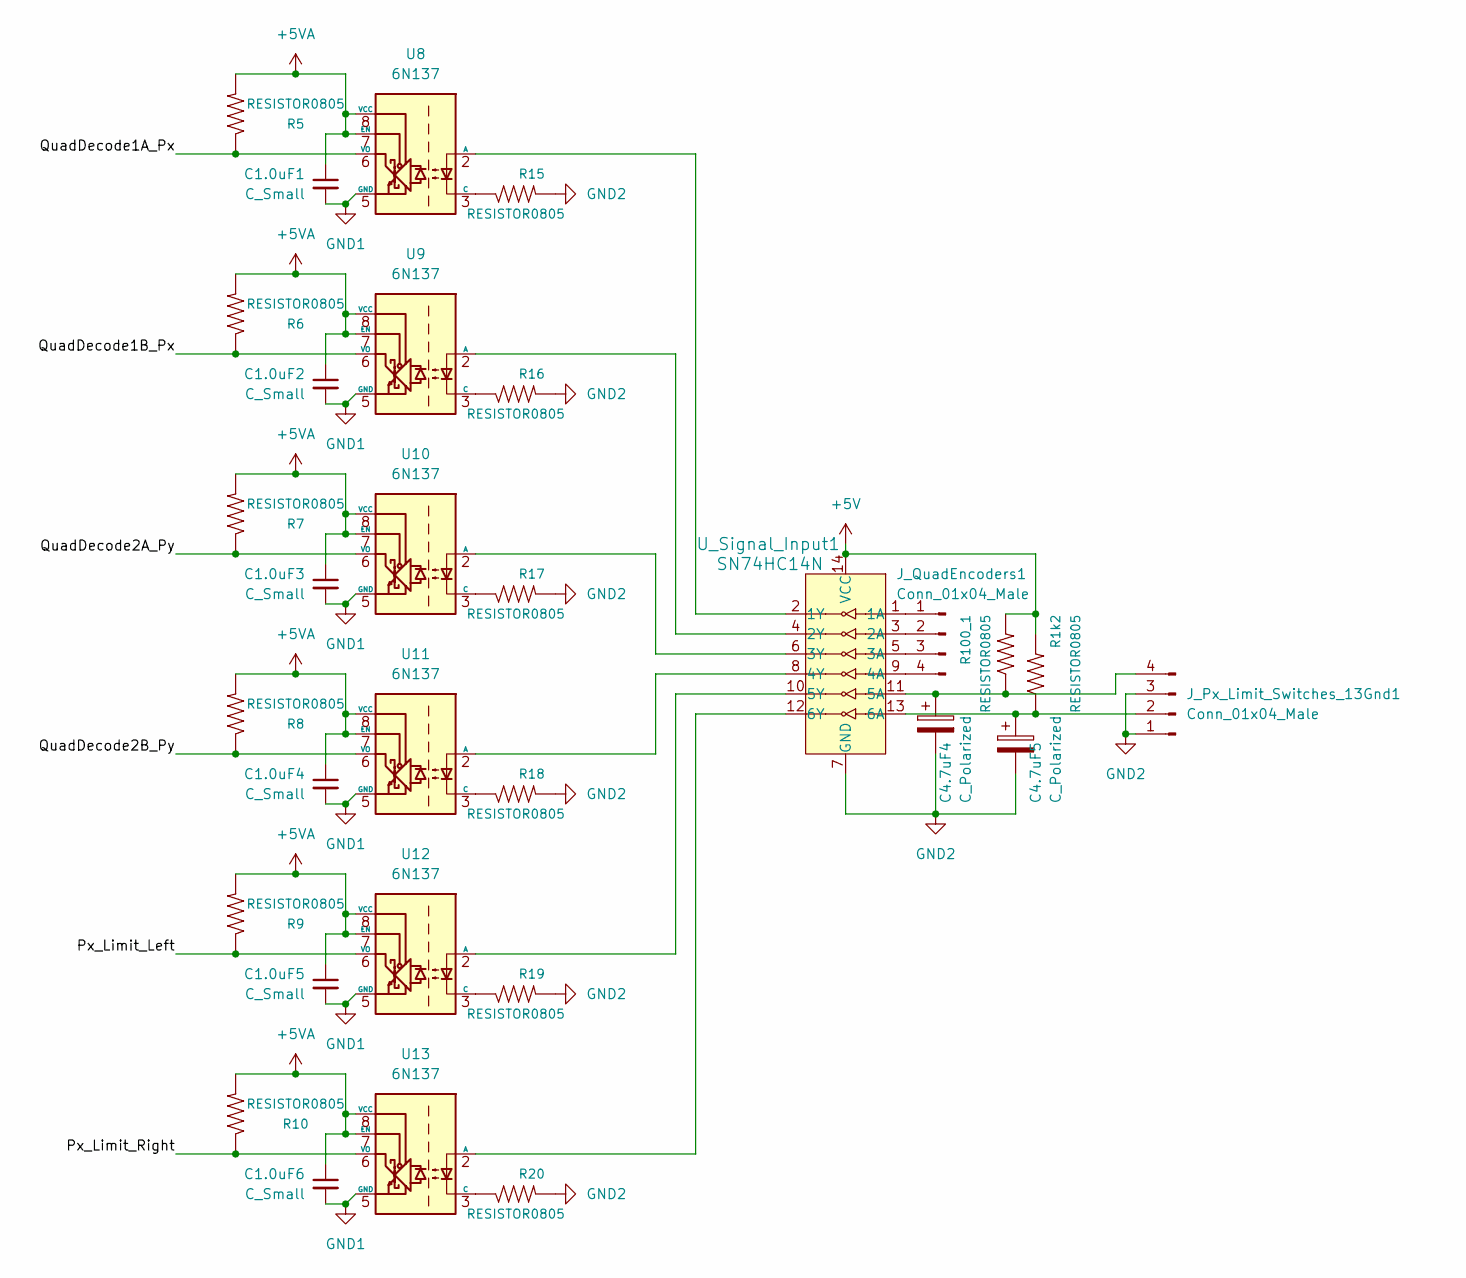
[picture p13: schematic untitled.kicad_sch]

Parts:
C1.0uF1, C1.0uF2, C1.0uF3, C1.0uF4, C1.0uF5, C1.0uF6: C_Small; C_0805_2012Metric_Pad1.18x1.45mm_HandSolder
C4.7uF4, C4.7uF5: C_Polarized; CP_Radial_D5.0mm_P2.00mm
J_Px_Limit_Switches_13Gnd1: Conn_01x04_Male; PinHeader_1x04_P2.54mm_Vertical
J_QuadEncoders1: Conn_01x04_Male; PinHeader_1x04_P2.54mm_Vertical
R1k2, R5, R6, R7, R8, R9, R10, R15, R16, R17, R18, R19, R20, R100_1: RESISTOR0805; R_0805_2012Metric_Pad1.20x1.40mm_HandSolder
U8, U9, U10, U11, U12, U13: 6N137; DIP-8_W7.62mm
U_Signal_Input1: SN74HC14N; DIP-14_W3mm; MPN SN74HC14N; Digi-Key_PN 296-1577-5-ND

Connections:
+5V: R1k2.2, R100_1.2, U_Signal_Input1.14 (VCC); also elsewhere on the board
+5VA: C1.0uF1.1, C1.0uF2.1, C1.0uF3.1, C1.0uF4.1, C1.0uF5.1, C1.0uF6.1, R5.2, R6.2, R7.2, R8.2, R9.2, R10.2, U8.7 (EN), U8.8 (VCC), U9.7 (EN), U9.8 (VCC), U10.7 (EN), U10.8 (VCC), U11.7 (EN), U11.8 (VCC), U12.7 (EN), U12.8 (VCC), U13.7 (EN), U13.8 (VCC); also elsewhere on the board
/Px_Limit_Left: R9.1, U12.6 (VO); also elsewhere on the board
/Px_Limit_Right: R10.1, U13.6 (VO); also elsewhere on the board
/QuadDecode1B_Px: R6.1, U9.6 (VO); also elsewhere on the board
/QuadDecode2A_Py: R7.1, U10.6 (VO); also elsewhere on the board
/QuadDecode2B_Py: R8.1, U11.6 (VO); also elsewhere on the board
GND1: C1.0uF1.2, C1.0uF2.2, C1.0uF3.2, C1.0uF4.2, C1.0uF5.2, C1.0uF6.2, U8.5 (GND), U9.5 (GND), U10.5 (GND), U11.5 (GND), U12.5 (GND), U13.5 (GND); also elsewhere on the board
GND2: C4.7uF4.2, C4.7uF5.2, J_Px_Limit_Switches_13Gnd1.1, J_Px_Limit_Switches_13Gnd1.3, R15.2, R16.2, R17.2, R18.2, R19.2, R20.2, U_Signal_Input1.7 (GND); also elsewhere on the board
unnamed: C4.7uF4.1, J_Px_Limit_Switches_13Gnd1.4, R100_1.1, U_Signal_Input1.11 (5A)
unnamed: C4.7uF5.1, J_Px_Limit_Switches_13Gnd1.2, R1k2.1, U_Signal_Input1.13 (6A)
unnamed: J_QuadEncoders1.1, U_Signal_Input1.1 (1A)
unnamed: J_QuadEncoders1.2, U_Signal_Input1.3 (2A)
unnamed: J_QuadEncoders1.3, U_Signal_Input1.5 (3A)
unnamed: J_QuadEncoders1.4, U_Signal_Input1.9 (4A)
unnamed: R16.1, U9.3 (C)
unnamed: R17.1, U10.3 (C)
unnamed: R18.1, U11.3 (C)
unnamed: R19.1, U12.3 (C)
unnamed: R20.1, U13.3 (C)
unnamed: U9.2 (A), U_Signal_Input1.4 (2Y)
unnamed: U10.2 (A), U_Signal_Input1.6 (3Y)
unnamed: U11.2 (A), U_Signal_Input1.8 (4Y)
unnamed: U12.2 (A), U_Signal_Input1.10 (5Y)
unnamed: U13.2 (A), U_Signal_Input1.12 (6Y)

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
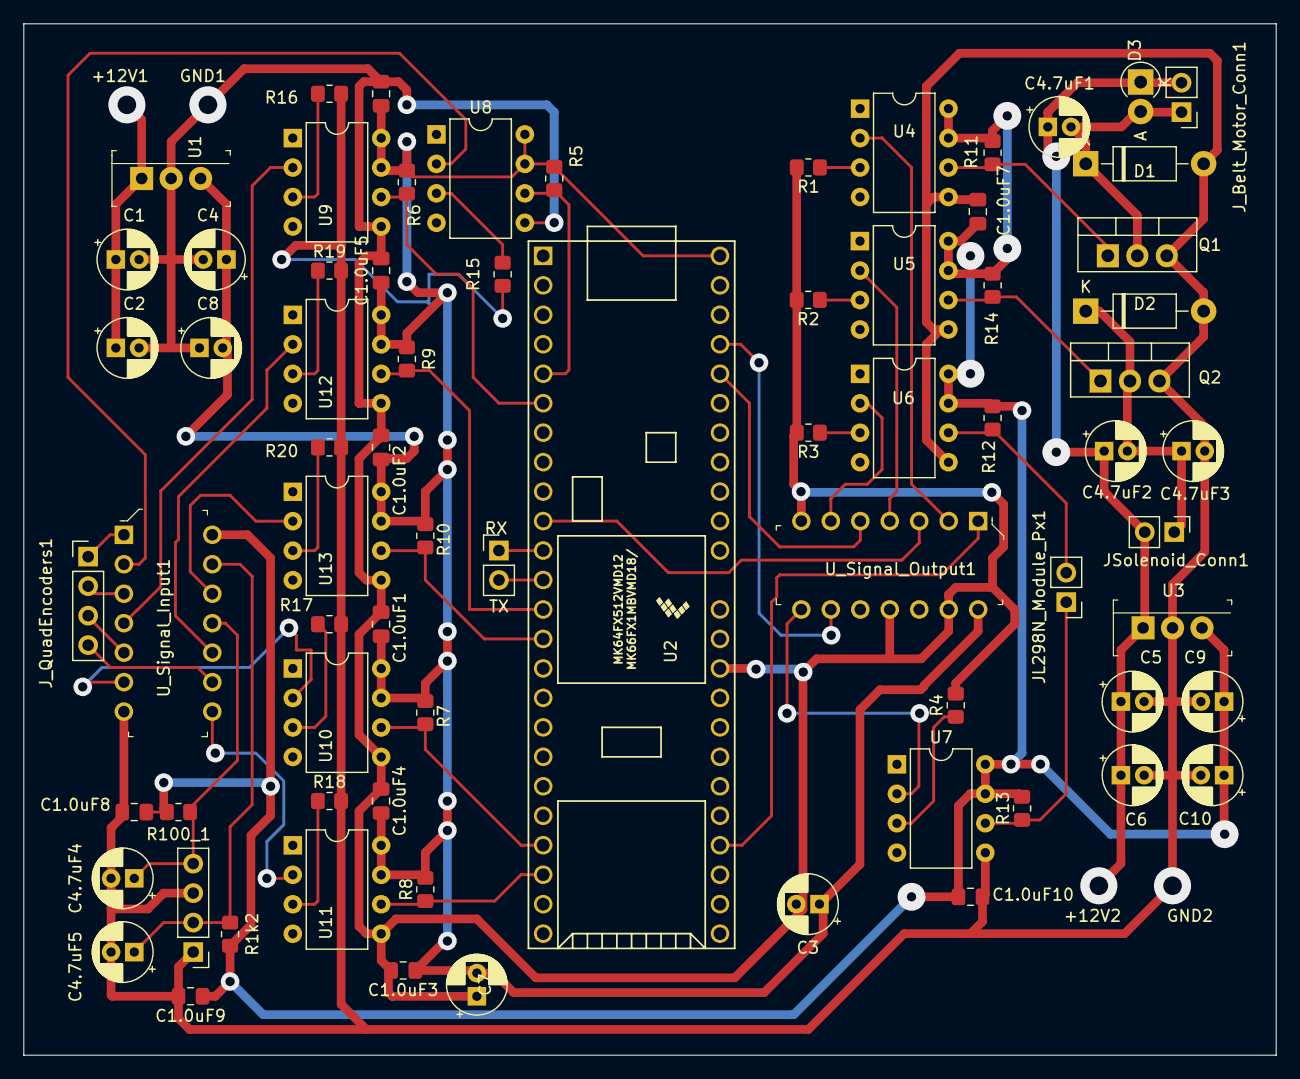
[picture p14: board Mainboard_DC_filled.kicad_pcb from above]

Board: 2 copper layers, 108.0 x 88.9 mm, 73 parts (0 on the bottom side), 48 nets.

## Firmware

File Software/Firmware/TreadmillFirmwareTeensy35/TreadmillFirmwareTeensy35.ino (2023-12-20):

#include "Arduino.h"
#include <FlexiTimer2.h>
#include "QuadDecode_def.h"

#include <stdbool.h>
#include "treadmillPinDefs.h"

#include <PID_v1.h>

#define HWSERIAL Serial2

const bool verboseMode = false;
double printLastPosY = 0;
double printLastPosX = 0;
//const int printSolenoid = 8; //NUMBER
double dropSpacing = 750; //1500; //250;
bool extendedPrint = false;
unsigned long printSolDur = 145;//145; 21Dec2022           //110; // 12.3 * 10; //12;
unsigned long printSolDurLong = 150;//115; //12.4 * 10; //12;
unsigned long printTimeThresh = 15000;
volatile bool resetPrintDur = false;
unsigned long lastPrintTime;
unsigned long keepWetPeriod = 20 * 1000; //10 * 1000;

#define MAX_SAMPLES_FLASH 10
#define PIN_isr 8
#define tripleLED 6
const unsigned long flashPer_us = 500000;
const double xPWMStallThresh = 0;

unsigned long PD_update_interval = 15000; // 25 msec update interval (PID interval will be double this)
unsigned long PX_update_interval = 2000; // 2msec update interval

unsigned long lastUpdate = 0; // Temporary debug variable

// Dynamic Variables ------------------------------------------------------------
volatile uint32_t tFlash[MAX_SAMPLES_FLASH];
volatile bool sFlash[MAX_SAMPLES_FLASH];
volatile int tFlashIter = 0;
volatile int flashUpdateLast = 0;
volatile bool flashUpdatePend = false;
unsigned long flashSyncLast = 0;

unsigned long curTimeMicros = 0;

const int strLength = 99;
const int outStrLength = 50;
char inputString[strLength];
char outputString[strLength];
char tempChar = '0';
int serPos = 0;
char checkStr[3];
char tempStr[3];
size_t checkVal = 0;

// Linear trail calc variables and constants
double PD_EQ_m = 0;
double PD_EQ_m_next = 0;

// Sine trail calc variables and constants
const double YSCALE = 5000;
double PD_EQ_a = 0;
double PD_EQ_T = 1;
double PD_EQ_ps = 0;
double PD_EQ_a_next = 0;
double PD_EQ_T_next = 1;
double PD_EQ_ps_next = 0;

// Shared trail calc variables
bool nextSin;
bool currSin;
double PD_EQ_start = 999999.01;
double PD_EQ_b = 0;
double PD_EQ_b_next = 0;

// Treadmill variables
double PD_SpeedRot = 0;
double PD_setSpeedRot = 0;
double PD_setPWM = 0;
double PD_Encoder_count = 0;
double PD_lastPos = 0;

// Print head variables
volatile bool PX_moveRightEnable  = false;
volatile bool PX_moveLeftEnable   = false;
double PX_pos = 0;
double PX_pos_exact = 0;
double PX_setPos = 0;
double PX_setPWM = 0;


// PID Settings
double PD_Kp = 2, PD_Ki = 4, PD_Kd = 0;
//kp: 0.32 ki: 0.01 kd: 0.00
PID PD_speed_PID(&PD_SpeedRot, &PD_setPWM, &PD_setSpeedRot, PD_Kp, PD_Ki, PD_Kd, DIRECT);

bool PX_round = false;
int PX_round_factor = 70;//10;

//double PX_Kp=1.5, PX_Ki=0.4, PX_Kd=.2;
//double PX_Kp = 2.5, PX_Ki = 0.4, PX_Kd = .2;
//double PX_Kp = 2.5, PX_Ki = 0.4, PX_Kd = 2.0;
double PX_Kp = 2.5, PX_Ki = 0.2, PX_Kd = 1.0;
PID PX_pos_PID(&PX_pos, &PX_setPWM, &PX_setPos, PX_Kp, PX_Ki, PX_Kd, P_ON_M, DIRECT);

elapsedMicros usTime;

// Functions  ------------------------------------------------------------
void LimitStopLeft() {
  //  if (verboseMode) {
  Serial.println("Left Limit Stop");
  //  }
  PX_moveLeftEnable = false;
  PX_moveRightEnable = true;
  analogWrite(printMotorLeft, 0);
  xPosn.zeroFTM(); //Zero Xposition counter
  Serial.println("X pos zeroed 1");
}

void LimitStopRight() {
  //  if (verboseMode) {
  Serial.println("Right Limit Stop");
  //  }
  PX_moveLeftEnable = true;
  PX_moveRightEnable = false;
  analogWrite(printMotorRight, 0);
}

void PX_ZeroPosition() {
  int testVal = digitalRead(PX_LimitLeft);
  if (testVal) {
    PX_moveLeftEnable = true;
    analogWrite(printMotorLeft, 110);
  } else {
    Serial.println("X pos zeroed 2");
    xPosn.zeroFTM(); //Zero Xposition counter
    PX_moveLeftEnable = false;
    PX_moveRightEnable = true;
  }
}

void PX_Output(double PX_setPWM) {
  if (micros() % 1000000 < 100) {
    Serial.print("PX_pos: ");
    Serial.print(PX_pos_exact);
    Serial.print("  PX_setPWM: ");
    Serial.print(PX_setPWM);
    Serial.print("  PX_moveLeftEnable: ");
    Serial.print(PX_moveLeftEnable);
    Serial.print("  PX_moveRightEnable: ");
    Serial.println(PX_moveRightEnable);
  }

  // Movement enable check
  if (!PX_moveLeftEnable) {
    if (!digitalRead(PX_LimitLeft)) {
      PX_moveLeftEnable = true;
    } else {
      Serial.println("X pos zeroed 3");
      xPosn.zeroFTM(); //Zero Xposition counter
    }
  }
  if (!PX_moveRightEnable) {
    if (!digitalRead(PX_LimitRight)) {
      PX_moveRightEnable = true;
    }
  }

  // PX Movement control
  if (PX_setPWM == 0) {
    analogWrite(printMotorLeft, 0);
    analogWrite(printMotorRight, 0);
  } else if (abs(PX_setPWM) > xPWMStallThresh) {
    if (PX_setPWM < 0 && PX_moveLeftEnable) {
      analogWrite(printMotorLeft, abs(PX_setPWM));
      analogWrite(printMotorRight, 0);
      //      Serial.print("Move Left set to "); Serial.println(PX_setPWM);
      PX_moveRightEnable = true;
    } else if (PX_setPWM > 0 && PX_moveRightEnable) {
      analogWrite(printMotorLeft, 0);
      analogWrite(printMotorRight, abs(PX_setPWM));
      //      Serial.print("Move Right set to "); Serial.println(PX_setPWM);
      PX_moveLeftEnable = true;
    }
  }
}

void PX_updateSetPos(bool updateNow = false) {
  double curY = -yPosn.calcPosn();
  double curX = xPosn.calcPosn();
  if (updateNow || curY >= PD_EQ_start) { // IF position cond. to use next print function is met
    // Log actual switchover PD value
    HWprint(254);
    HWprint(curY);
    HWprintln(usTime);

    // Zero PD Position
    yPosn.zeroFTM();

    // Update previous position so PD speed estimate is correct
    double temp_offset = curY - PD_lastPos;
    PD_lastPos = -temp_offset;
    Serial.print("Before Y: "); Serial.println(printLastPosY);
    printLastPosY = curY - printLastPosY;
    Serial.print("After Y: "); Serial.println(printLastPosY);
    Serial.print("Before X: "); Serial.println(printLastPosX);
    printLastPosX = curX - printLastPosX;
    Serial.print("After X: "); Serial.println(printLastPosX);


    // Update position function to new values
    if (nextSin) {
      currSin = true;
      PD_EQ_a = PD_EQ_a_next;
      PD_EQ_T = PD_EQ_T_next;
      PD_EQ_ps = PD_EQ_ps_next;
      PD_EQ_b = PD_EQ_b_next;
    } else {
      currSin = false;
      PD_EQ_m = PD_EQ_m_next;
      PD_EQ_b = PD_EQ_b_next;
    }
  }
  // Regardless, update xPosn goal
  if (currSin) {
    PX_setPos = round(PD_EQ_a * sin(2 * M_PI * 1 / PD_EQ_T * (curY + PD_EQ_ps))) + PD_EQ_b;
  } else {
    PX_setPos = round(PD_EQ_m * curY) + PD_EQ_b;
  }

  if (PX_round) {
    PX_setPos = round(PX_setPos / PX_round_factor);
  }
}

void readSerial() {
  if (HWSERIAL.available() > 0) {
    tempChar = HWSERIAL.read();
    if (tempChar == '<') { // Beginning of new message
      serPos = 0;
      for (int iter = 0; iter < strLength; iter++) {
        inputString[iter] = '\0';
      }
    } else if (tempChar == '>') { // End of message - process
      //      Serial.print("AAAAARGH:  ");
      //      Serial.println(inputString);

      // Check if received message is complete
      checkStr[0] = inputString[0];
      checkStr[1] = inputString[1];
      checkStr[2] = '\0';
      checkVal = atoi(checkStr);



      if (checkVal == strlen(inputString)) {
        // If message is not missing parts process message
        if (inputString[3] == '1') {      // Motor speed update
          //          Serial.println("Speed update received");
          parseSerialSpeed(inputString, strLength, &PD_setSpeedRot);
        } else if (inputString[3] == '2') { // Print function update
          //          Serial.println("Lin func received");
          parseSerialFunc(inputString, strLength, &PD_EQ_m_next, &PD_EQ_b_next, &PD_EQ_start, &nextSin);
        } else if (inputString[3] == '3') { // PID Tuning update
          //          Serial.println("PID Update received");
          parseSerialPX_PID(inputString, strLength, &PX_Kp, &PX_Ki, &PX_Kd);
          //        } else if (inputString[3] == '4') { // Print function update - IMMEDIATE UPDATE
          //          parseSerialFuncImm(inputString, strLength, &PD_EQ_m_next, &PD_EQ_b_next, &PD_EQ_start);
        } else if (inputString[3] == '6') { // Sin function serial
          //          Serial.println("Sin func received");
          parseSerialFuncSin(inputString, strLength, &PD_EQ_a_next, &PD_EQ_T_next, &PD_EQ_ps_next, &PD_EQ_b_next, &PD_EQ_start, &nextSin);
        } else {
          Serial.print("ERROR: Command unknown: ");// ignore - command is not known
          Serial.println(inputString);
        }
      } else {
        Serial.println("ERROR: Message corrupted: ");
        Serial.println(inputString);
        // If message IS missing parts send error message and timestamp
        HWprint(250);
        HWprint(checkVal);
        HWprint("(");
        HWprint(inputString);
        HWprint(")");
        HWprintln(usTime);
      }
    } else { // Continue adding to message
      inputString[serPos] = tempChar;
      if (serPos < (strLength - 1)) {
        serPos += 1;
      }
    }
  }
}

void parseSerialSpeed(char inputString[], const int strLength, double * PD_setSpeedRot) {
  char * temp;
  char delim = ',';
  temp = strtok(inputString, &delim); // Remove length checksum & com flag
  temp = strtok(NULL, &delim);        // call again to retrieve second str token
  temp = strtok(NULL, &delim);        // call again to retrieve third str token
  *PD_setSpeedRot = atoi(temp);
  if (verboseMode) {
    Serial.print("Speed set to ");
    Serial.println(*PD_setSpeedRot);
  }
}

void parseSerialFunc(char inputString[], int strLength, double * PD_EQ_m_next, double * PD_EQ_b_next, double * PD_EQ_start, bool * nextSin) {
  //  Serial.print("parseSerialFunc: ");
  //  Serial.println(inputString);

  // Set next function transition to linear
  *nextSin = false;

  // Parse
  char * temp;
  char delim = ',';
  temp = strtok(inputString, &delim); // Remove length checksum & com flag
  temp = strtok(NULL, &delim);
  temp = strtok(NULL, &delim);        // call again to retrieve third str token
  *PD_EQ_m_next = atof(temp);
  temp = strtok(NULL, &delim);
  *PD_EQ_b_next = atof(temp);
  temp = strtok(NULL, &delim);
  *PD_EQ_start = atof(temp);

  // Check whether to set immediately
  temp = strtok(NULL, &delim);
  int startImm = atoi(temp);

  if (startImm == 1) {
    Serial.println("Start immediately");
    PX_updateSetPos(true);
  }

  if (verboseMode) {
    Serial.print("  setM: ");
    Serial.print(*PD_EQ_m_next);
    Serial.print("  setB: ");
    Serial.println(*PD_EQ_b_next);
  }
}
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

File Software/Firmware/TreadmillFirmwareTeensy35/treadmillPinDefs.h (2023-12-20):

// Settings
double defSpeed = 150; // deg/s
double sensitivity = .1; // convert speed difference into PWM difference
const double xTolerance = 5; // Number of increments past target before reversing direction to correct.
const int prSpeed = 120;
int checkThresh = 10;

// Definitions ------------------------------------------------------------
QuadDecode<2> yPosn;  // Template using FTM1
QuadDecode<1> xPosn;  // Template using FTM2

// Paper Drive
//int beltMotorFW   = 21; // Paper Drive Motor Forwards
int beltMotorFW = 22; // changed during march 2022 pcb update... 36; // Changed during belt motor transfer repair Oct 2021
int beltMotorRev  = 20; // reverse

const int PX_LimitLeft  = 11;  // Printer X Limit Switch Left
const int PX_LimitRight = 12;
const int printMotorLeft  = 36; // changed during march 2022 pcb update...22; // Printer X Motor left
const int printMotorRight = 23; // right

const int printSolenoid = 8;

const int left = -1;
const int right = 1;
const int forwards = 1;
const int backwards = -1;

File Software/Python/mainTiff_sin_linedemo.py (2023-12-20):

import sys

import numpy as np
import cv2
import math
import serial
import time
import os
import re
import multiprocessing as mp

import tiffile
import imagecodecs

# Settings
width = 1920  # Range is 0-1438 at far right
scale = 16
verbose = True
serMaxSize = 50
serInterval = 0.1  # 10Hz update rate on speed
nTiffIms = 200
saveDirectory = "C:/Users/grays/Documents/TreadmillData/"  # Directory where folder of images and data should be stored

# Sub-function storage for now ---------------------------------------------------

# !/usr/bin/python3 Excellent wrapper from @skoehler (https://github.com/pyserial/pyserial/issues/216)
class ReadLine:
    def __init__(self, s):
        self.buf = bytearray()
        self.s = s

    def readline(self):
        i = self.buf.find(b"\n")
        if i >= 0:
            r = self.buf[:i + 1]
            self.buf = self.buf[i + 1:]
            return r
        while True:
            i = max(1, min(2048, self.s.in_waiting))
            data = self.s.read(i)
            i = data.find(b"\n")
            if i >= 0:
                r = self.buf + data[:i + 1]
                self.buf[0:] = data[i + 1:]
                return r
            else:
                self.buf.extend(data)

def calcSpeed(verbose, width, cap, savedir, imDatafile, imCounter, outIter, nTiffIms, centDatafile):
    # Capture frame
    frame = cap.read()[1]

    timestamp = time.time()  # temporary until better frame timestamp is figured out
    # frame = frame[:, 240:1680]
    # frame2 = frame[170:865, 260:1670]
    # gray = cv2.cvtColor(frame2, cv2.COLOR_BGR2GRAY)
    gray = cv2.cvtColor(frame, cv2.COLOR_BGR2GRAY)
    # bw = cv2.threshold(gray, 80, 255, cv2.THRESH_BINARY_INV)[1] # Backlight off
    bw = cv2.threshold(gray, 20, 255, cv2.THRESH_BINARY_INV)[1] # Backlight on
    # bw = cv2.threshold(gray, 80, 255, cv2.THRESH_BINARY_INV)[1]  # IR Backlight
    # bw = cv2.threshold(gray, 40, 255, cv2.THRESH_BINARY_INV)[1]  # IR Backlight

    # Erode image
    # kernel = np.ones((5, 5), np.uint8)
    # erosion = cv2.erode(bw, kernel, iterations=1)

    # calculate x,y coordinate of center
    try:
        contours = cv2.findContours(bw, 1, 1)[0]
        # contours = cv2.findContours(erosion, 1, 1)[0]
        c = max(contours, key=cv2.contourArea)
        M = cv2.moments(c)  # calculate moments of binary image

        # M = cv2.moments(erosion)  # calculate moments of binary image
        cX2 = int(M["m10"] / M["m00"])
        cY2 = int(M["m01"] / M["m00"])
        center = (cX2, cY2)
        # print(center)
        # Calculate speed setting
        if cX2 > round(width / 2):
            speed = 0
        else:
            normalX = scale * (width / 2 - cX2) / width
            speed = math.exp(normalX) - math.exp(0)
        # print(speed)

    except:
        print("Locust not seen")
        cX2 = 0
        cY2 = 0
        center = (cX2, cY2)
        speed = 0 # Stop treadmill if locust disappeared

    # if verbose:
        # Edit frame and show on screen
        # masked = cv2.bitwise_and(frame, frame, mask=erosion)
        # drawn = cv2.circle(frame, center, 5, (0, 255, 0), 2)
        # cv2.imshow("windowName", drawn)

    # drawn = cv2.circle(frame, center, 5, (0, 255, 0), 2)
    # cv2.imshow("windowName", drawn)
    # cv2.imshow("windowName", frame)
    # cv2.imshow("windowName", bw)
    cv2.waitKey(1)
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

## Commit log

2023-12-15 Added Electrical, Mechanical Files
    [Mainboard_DC_filled.kicad_pcb, Mainboard_DC_filled.kicad_sch, untitled.kicad_sch]
2023-12-20 Fixed PCB Error
    [Mainboard_DC_filled.kicad_pcb, Mainboard_DC_filled.kicad_sch, untitled.kicad_sch]
2023-12-20 Updated instructions
    Added print carriage insert reference photos, updated readme
